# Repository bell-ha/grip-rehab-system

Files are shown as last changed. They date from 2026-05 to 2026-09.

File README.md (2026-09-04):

<div align="center">

# 악력 재활 시스템

**로드셀에서 읽은 힘을 실시간 신호처리로 다듬어, 게임과 소리로 되돌려주는 재활 시스템**







단국대학교 임베디드 시스템 과제 · 2인 팀 · 2026.04 ~ 2026.07

</div>

<div align="center">

<a href="https://www.youtube.com/watch?v=_I-ejlEAkNM">

</a>

<sub>데모 영상 — 로드셀을 쥐는 힘이 그대로 게임 입력이 된다 &nbsp;·&nbsp; 이미지를 누르면 영상이 열린다</sub>

<br><br>

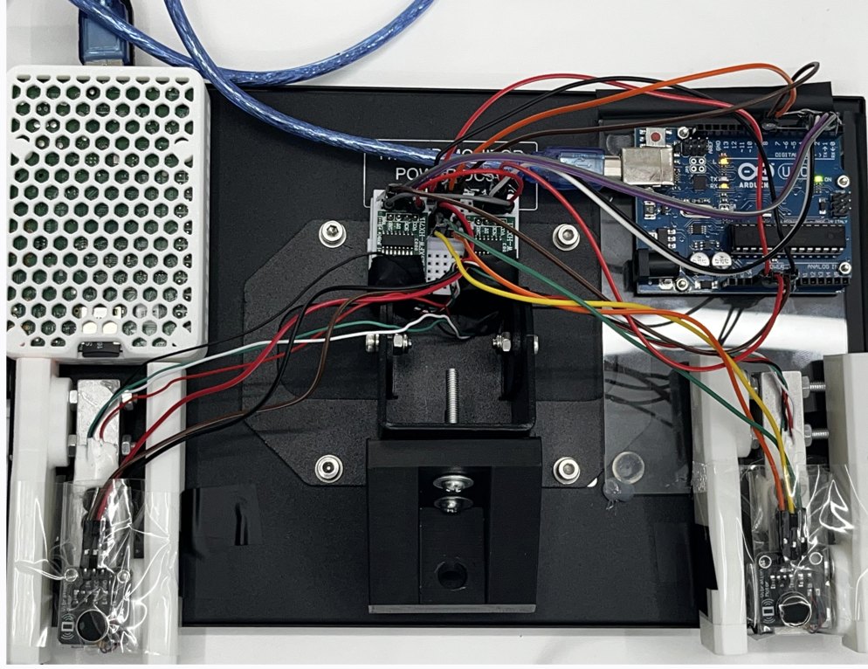
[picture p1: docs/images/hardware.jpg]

<br><sub>가운데 로드셀 마운트(3D 모델링·출력), 우측 상단 아두이노 우노, 그 아래 HX711 증폭 모듈.<br>좌우 진동 모터는 전류 부하 때문에 트랜지스터 구동으로 회로를 바꿨다</sub>

</div>

---

## 한눈에 보기

| | |
|---|---|
| **문제** | 악력 재활 훈련은 반복적이고 지루해서 지속률이 낮다 |
| **접근** | 양손 악력을 실시간으로 읽어 **게임 조작과 소리**로 되돌려준다 |
| **엔지니어링 초점** | 로드셀 원신호는 **노이즈와 스파이크로 그대로 쓸 수 없다.** 이걸 게임 입력으로 쓸 수 있는 신호로 만드는 것이 핵심 |
| **핵심 설계** | ① 4단 필터 파이프라인 ② 센서 3종 추상화 ③ Producer–Consumer 60 Hz 루프 |
| **결과** | 재활 게임 3종 + 악력 신디사이저 1종, 런처까지 손만으로 조작 |

> 이 저장소는 "게임 4개"가 아니라 **"센서 신호를 실시간 제어 입력으로 만드는 파이프라인"**에 관한 것이다.
> 게임은 그 파이프라인을 검증하는 응용이다.

---

## 목차

1. [왜 신호처리가 핵심인가](#1-왜-신호처리가-핵심인가)
2. [시스템 구성](#2-시스템-구성)
3. [신호처리 파이프라인](#3-신호처리-파이프라인)
4. [센서 3종 추상화](#4-센서-3종-추상화)
5. [실행 구조 (Producer–Consumer)](#5-실행-구조-producerconsumer)
6. [하드웨어](#6-하드웨어)
7. [응용 — 게임 3종 + 신디사이저](#7-응용--게임-3종--신디사이저)
8. [캘리브레이션](#8-캘리브레이션)
9. [실행 방법](#9-실행-방법)
10. [겪은 문제와 해결](#10-겪은-문제와-해결)

---

## 1. 왜 신호처리가 핵심인가

HX711 로드셀은 80 Hz로 값을 뱉지만, 그 원신호는 **게임 입력으로 바로 쓸 수 없다.**

- 손이 닿는 순간 **수십 kg짜리 스파이크**가 튄다
- 힘을 유지해도 값이 **미세하게 계속 진동**한다
- 손을 뗀 상태에서도 **0이 아니라 1 kg 근처를 떠돈다**

이 상태로 게임에 연결하면 캐릭터가 떨리고, 의도하지 않은 입력이 들어가고, 손을 뗐는데도 조작이 계속된다. **재활 대상자가 쓰는 시스템에서 이건 곧 사용 불가를 의미한다.**

그래서 이 프로젝트의 실제 과제는 게임을 만드는 것이 아니라, **원신호를 신뢰할 수 있는 제어 입력으로 바꾸는 것**이었다.

---

## 2. 시스템 구성

```mermaid
flowchart LR
    LC["로드셀 ×2<br/>좌 / 우"] --> ADC["HX711 ADC ×2<br/>80 Hz"]
    ADC --> ARD["Arduino Uno"]
    ARD -->|"UART 115200<br/>raw,raw"| PY["Python 런타임"]
    PY -->|"L1/L0/R1/R0"| ARD
    ARD --> VIB["진동 액츄에이터 ×2<br/>PWM"]

    PY --> FILT["4단 필터<br/>파이프라인"]
    FILT --> GAME["게임 루프<br/>60 Hz 고정 dt"]
    GAME --> SFX["오디오 피드백"]

    style FILT fill:#1f6feb,color:#fff
    style GAME fill:#1f6feb,color:#fff
```

**양방향 통신**이다. 센서 값을 받기만 하는 게 아니라, 게임 이벤트(두더지 명중, 벽 충돌)가 발생하면 진동 명령을 되돌려 보낸다.

---

## 3. 신호처리 파이프라인

원신호 → 제어 입력까지 4단계.

```mermaid
flowchart LR
    A["raw<br/>80 Hz"] --> B["① 스파이크 제거<br/>Δ &gt; 8 kg 폐기"]
    B --> C["② 중간값 필터<br/>N = 3"]
    C --> D["③ 이동평균<br/>N = 5"]
    D --> E["④ 데드존<br/>&lt; 1 kg → 0"]
    E --> F["kg"]

    style B fill:#1f6feb,color:#fff
    style C fill:#1f6feb,color:#fff
    style D fill:#1f6feb,color:#fff
    style E fill:#1f6feb,color:#fff
```

| 단계 | 파라미터 | 잡아내는 문제 |
|---|---|---|
| ① **스파이크 제거** | 이전 값 대비 **8 kg** 이상 급변 시 폐기 | 손이 닿는 순간의 순간 피크, 케이블 흔들림 |
| ② **중간값 필터** | 윈도우 **3** | 산발적 이상치. 평균과 달리 이상치에 끌려가지 않음 |
| ③ **이동평균** | 윈도우 **5** | 유지 구간의 미세 진동 |
| ④ **데드존** | **1 kg** 미만 → 0 | 손을 뗀 상태의 잔류값. "안 쥐고 있음"을 확실히 0으로 |

**순서가 설계 지점이다.** 스파이크를 먼저 버리지 않으면 중간값·이동평균 윈도우가 오염되고, 데드존을 먼저 적용하면 스파이크가 그대로 통과한다.

구현: [`common/sensor.py`](common/sensor.py)

---

## 4. 센서 3종 추상화

`GripSensor` 추상 인터페이스 하나에 구현 3개를 두었다.

| 구현 | 입력원 | 용도 |
|---|---|---|
| `MockGripSensor` | **키보드** (A/S 왼손, K/L 오른손) | **하드웨어 없이 게임 로직 개발·테스트** |
| `ArduinoGripSensor` | USB 시리얼 `raw,raw` | 일반 PC + Arduino |
| `RealGripSensor` | Raspberry Pi GPIO 직결 | 최종 배포 형태 |

**Mock 구현이 실용적으로 가장 중요했다.** 로드셀·Arduino가 없는 자리에서도 게임 로직과 렌더링을 그대로 개발할 수 있었고, 하드웨어 문제와 소프트웨어 문제를 분리해서 디버깅할 수 있었다.

Mock은 단순 키 입력이 아니라 실제 악력의 거동을 흉내 낸다 — 누르고 있으면 **9 kg/s로 차오르고**, 떼면 **8 kg/s로 감소**한다.

게임 코드는 어느 구현이 붙어 있는지 알지 못한다. 실행 플래그(`--arduino` / `--real` / 없음)만 바꾸면 된다.

---

## 5. 실행 구조 (Producer–Consumer)

센서는 **80 Hz**, 게임 루프는 **60 Hz**다. 주기가 다르고, 시리얼 읽기는 블로킹이다.

```
[센서 스레드]  시리얼 read → 필터 → Queue.put()      80 Hz
                                   │
[메인 스레드]  Queue.get_nowait() → 게임 로직 → 렌더  60 Hz 고정 dt
```

메인 루프에서 직접 시리얼을 읽으면 **읽기 지연이 그대로 프레임 드롭**이 된다. 센서 읽기를 별도 스레드로 분리하고 큐로 넘겨, 게임 루프가 센서 상태와 무관하게 일정한 dt를 유지하도록 했다.

고정 dt를 쓴 이유는, 물리 계산(풍선 팽창 속도, 우주선 관성)이 프레임 레이트에 따라 달라지면 **같은 힘을 줘도 기기마다 다르게 동작**하기 때문이다.

---

## 6. 하드웨어

### 배선

| 신호 | 왼손 | 오른손 |
|---|---|---|
| HX711 DOUT | D2 | D4 |
| HX711 SCK | D3 | D5 |
| 진동 액츄에이터 | D9 (PWM) | D10 (PWM) |

Raspberry Pi 직결 시 (BCM): DOUT `GPIO 5` / `GPIO 13`, SCK `GPIO 6` / `GPIO 19`

### 시리얼 프로토콜

직접 설계한 최소 프로토콜이다.

```
Arduino → PC   (10 ms 주기)      285400,291820\n     좌 raw, 우 raw
PC → Arduino   (이벤트 발생 시)   L1 / L0 / R1 / R0    좌우 진동 ON/OFF
```

파싱 비용을 줄이기 위해 고정 포맷 한 줄로 유지했고, 진동 명령은 상태 토글 방식이라 게임 쪽에서 타이머를 관리하지 않아도 된다.

### 3D 프린팅 마운트

로드셀을 손으로 쥘 수 있는 형태로 고정하기 위해 직접 모델링·출력했다.

| 파일 | 설명 |
|---|---|
| [`models/Base_1.stl`](models/Base_1.stl) | 센서 고정 베이스 |
| [`models/HX711_Load_Cell--Foot.stl`](models/HX711_Load_Cell--Foot.stl) | 로드셀 발판 |

---

## 7. 응용 — 게임 3종 + 신디사이저

파이프라인이 제대로 동작하는지는 **서로 다른 성격의 입력 요구**로 검증했다.

| 응용 | 요구하는 입력 특성 | 검증하는 것 |
|---|---|---|
| **풍선 키우기** | 목표값(≈15 kg)을 3초간 **유지** | 정상 상태의 안정성 — 진동이 남으면 유지 판정이 깨진다 |
| **두더지 잡기** | 짧고 강한 **순간 입력** | 응답 지연 — 필터가 과하면 반응이 늦어진다 |
| **우주 조종** | 양손 **차이값**으로 연속 조향 | 좌우 채널의 균형 — 한쪽만 편향되면 계속 휜다 |
| **악력 신디사이저** | 힘 → **연속적인 소리** | 미세 변화 해상도 — 떨림이 그대로 음정 흔들림이 된다 |

**신디사이저가 가장 가혹한 검증이었다.** 시각 피드백은 약간의 떨림을 눈치채기 어렵지만, 소리는 즉시 드러난다. 왼손이 볼륨(0.5~15 kg), 오른손이 주파수(2.3 kg → 220 Hz ~ 10 kg → 600 Hz, 로그 스케일)를 맡고, 기본파 + 2배음 + 3배음을 합성해 `aplay`로 끊김 없이 PCM 스트리밍한다.

**런처도 손으로 조작한다** — 왼손 0.3초 유지로 커서 왼쪽, 오른손으로 오른쪽, 양손 유지로 선택. 키보드 없이 시스템 전체를 쓸 수 있어야 재활 도구로 성립한다.

모든 게임 공통 종료 제스처: **양손 더블 펌프**(2초 내 2번 힘껏)

---

## 8. 캘리브레이션

로드셀은 개체마다 스케일이 다르고, 조립 상태에 따라 영점이 달라진다. 매번 손으로 맞출 수 없으므로 자동화했다.

**Arduino 모드 — 자동** (첫 실행 시)
```
1. 영점(Tare) 3초   손을 떼세요
2. 최대 악력 5초    최대한 세게 쥐세요
3. common/calibration.json 저장 → 이후 실행부터 재사용
```

**Raspberry Pi 직결 — 수동** ([`games/balloon_game/calibrate.py`](games/balloon_game/calibrate.py))
알고 있는 무게를 올려 스케일 팩터를 계산한다.

---

## 9. 실행 방법

```bash
python3 -m venv venv && source venv/bin/activate
pip install -r requirements.txt
```

Raspberry Pi에서 HX711 직결 시: `sudo apt-get install python3-dev alsa-utils && pip install hx711`

**런처** (전체 진입점)
```bash
cd games
DISPLAY=:0 python3 launcher.py --arduino   # Arduino USB
DISPLAY=:0 python3 launcher.py --real      # Pi HX711 직결
```

**개별 게임** — 3가지 모드 공통
```bash
python3 main.py            # Mock — 센서 없이 키보드로 (A/S 왼손, K/L 오른손)
python3 main.py --arduino  # Arduino USB 포트 자동 감지
python3 main.py --real     # Raspberry Pi GPIO 직결
```

**디버그 — 시리얼 모니터**
```bash
python3 measure/main.py    # 1/2 왼쪽 진동, 3/4 오른쪽 진동, q 종료
```

---

## 10. 겪은 문제와 해결

**진동 모터를 켜면 오른손 센서 값이 끊긴다**
진동 액츄에이터를 GPIO에 직결했더니 순간 전류가 몰려 HX711 읽기가 불안정해졌다. **NPN 트랜지스터(2N2222)를 통해 구동**하도록 회로를 바꿔 해결했다. 소프트웨어 문제로 보였지만 원인은 전원이었다.

**필터를 강하게 걸면 반응이 느려진다**
이동평균 윈도우를 키우면 신호는 매끄러워지지만 두더지 잡기의 반응속도가 떨어진다. **윈도우 3(중간값) + 5(이동평균)** 조합이 안정성과 지연 사이의 균형점이었다.

**포트 충돌**
Arduino IDE 시리얼 모니터가 열려 있으면 Python이 포트를 잡지 못한다. 포트 자동 감지를 넣되, 실패 시 원인을 명시하도록 했다.
포트 확인: macOS `ls /dev/cu.*` · Linux `ls /dev/ttyUSB*` `ls /dev/ttyACM*`

---

## 저장소 구조

```
├── sketch_jun11a.ino          # Arduino 펌웨어 (HX711 읽기 + 진동 제어)
├── common/                    # ★ 공용 계층
│   ├── sensor.py              #   GripSensor 추상화 + 필터 파이프라인
│   ├── sfx.py                 #   절차적 효과음 (numpy 합성)
│   └── fonts.py
├── games/
│   ├── launcher.py            #   메인 진입점 (악력으로 조작)
│   ├── balloon_game/          #   main / game_logic / renderer / calibrate
│   ├── Whack-A-Mole/          #   main / game_logic / renderer
│   ├── steering_game/         #   main / game_logic / renderer
│   └── synthesizer/           #   main / audio_engine / renderer
├── measure/main.py            # 시리얼 모니터 (디버그)
└── models/*.stl               # 3D 프린팅 마운트
```

`common/`에 하드웨어 접근과 신호처리를 한 벌만 두고, 그 위에 응용을 올리는 구조다. 센서 프로토콜이나 필터가 바뀌어도 `common/` 한 곳만 고치면 전체에 반영된다. 각 응용은 `main` / `game_logic` / `renderer`로 동일하게 분리했다.

---

<div align="center">

**이종하** · [GitHub](https://github.com/bell-ha) · [Portfolio](https://bell-ha.github.io)

</div>

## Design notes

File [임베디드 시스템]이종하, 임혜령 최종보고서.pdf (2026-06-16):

# 스마트 악력 측정 및 재활 게임 시스템

## 노인 재활을 위한 양손 악력 측정 기반

## 멀티 게임 시스템의 설계 및 구현

단국대학교 컴퓨터공학과

과목: 임베디드 시스템

학번 / 성명 : 32203482 이종하

학번 / 성명 : 32223872 임혜령

제출일 : 2026. 6. 16.

목차

1. 초록 | 1
2. 서론 | 2
3. 관련 연구 | 3
4. 시스템 설계 | 4
4.1 전체 아키텍처 | 4
4.2 하드웨어 설계 | 5
4.3 소프트웨어 설계 | 6
5. 구현 | 8
5.1 하드웨어 제작 | 8
5.2 핵심 코드 | 8
5.3 게임 구현 | 10
6. 결론 | 15
7. 참고문헌 | 16

## 1. 초록

본 연구는 손 악력이 저하된 노인 및 인지 기능 저하 환자를 대상으로, 재활 훈련을 게임의

형태로 제공하는 임베디드 악력 재활 게임기를 설계하고 구현한 결과를 기술한다.

제안하는 시스템은 두 개의 로드셀과 HX711 아날로그-디지털 변환(ADC) 모듈을 이용하여

양손의 악력을 동시에 측정하고, 아두이노가 이를 디지털 수치로 변환하여 USB UART

시리얼 통신으로 라즈베리 파이 4에 전송하며, 라즈베리 파이는 Pygame 기반의 게임

로직과 화면 출력을 담당한다. 아두이노는 악력 데이터 송신뿐 아니라 라즈베리

파이로부터 진동 명령을 수신하여 좌우 손잡이에 내장된 코인 진동 모터를 독립적으로

구동하는 양방향 시리얼 통신 구조를 채택하였다.

악력 신호의 미세한 떨림과 잡음을 제거하기 위하여 스파이크 필터, 중간값 필터, 이동

평균 필터, 데드존으로 구성된 다단계 신호 처리 파이프라인을 적용하였으며, 게임 진행

상태는 유한 상태 머신으로 모델링하였다. 사용자 상호작용은 마우스나 키보드 없이 오직

악력만으로 이루어지도록 설계하였다. 총 네 가지 게임, 즉 근력 조절 훈련의 '풍선 키우기',

반응 속도 및 좌우 인지 판단의 '두더지 잡기', 양손 힘의 차이를 이용하는 '우주선 조종',

그리고 악력을 음악적 표현으로 연결하는 '악력 신디사이저'를 구현하였다. 악력기 본체는

3D 프린팅으로 제작하였으며, 진동 모터를 손잡이 내부에 내장하여 시각·청각·촉각의 다중

감각 재활 UX를 실현하였다.

구현 결과 제안 시스템은 저비용 부품만으로 양손 악력을 안정적으로 측정하고 이를

다양한 게임 피드백에 실시간으로 반영함으로써, 노인 사용자가 흥미를 유지하며 재활에

참여할 수 있는 통합형 플랫폼으로서의 가능성을 확인하였다.

## 2. 서론

전 세계적으로 고령 인구의 비율이 급격히 증가하고 있으며, 우리나라 또한 초고령

사회로의 진입을 앞두고 있다. 고령화에 따라 뇌졸중, 파킨슨병, 근감소증 등으로 인한

상지(上肢) 기능 저하 환자가 늘어나고 있으며, 이들에게 있어 손의 악력은 일상생활 수행

능력 및 전반적 건강 상태를 가늠하는 중요한 지표로 알려져 있다. 특히 악력은 노인의

근력 수준뿐 아니라 사망률과 인지 기능 저하를 예측하는 임상적 지표로도 활용되고 있어,

지속적인 측정과 훈련의 필요성이 강조된다.

그러나 기존의 재활 방식은 여러 한계를 지닌다. 첫째, 단순 반복 동작 위주의 전통적 재활

운동은 환자에게 지루함을 유발하여 장기적인 참여 동기를 떨어뜨린다. 둘째, 측정과

훈련이 분리되어 있어 환자의 재활 경과를 정량적으로 누적·관리하기 어렵다. 셋째, 상용

재활 장비는 고가이며 대형 의료기관에 한정되어 있어 접근성이 낮다. 넷째, 인지 기능이

저하된 노인의 경우 복잡한 조작이나 규칙을 요구하는 장비는 사용 자체가 어렵다.

본 연구는 이러한 문제를 해결하기 위하여 측정·훈련·피드백을 하나로 통합한 저비용 악력

재활 게임 시스템을 제안한다. 제안 시스템은 (1) 로드셀과 HX711을 이용해 양손 악력을

정밀하게 측정하고, (2) 측정값을 네 가지 게임의 즉각적 시각·촉각 피드백으로 변환하여

재미와 동기를 부여하며, (3) 악력만으로 모든 상호작용이 가능하도록 설계하여 인지 저하

환자의 사용성을 확보하는 것을 목표로 한다. 또한 아두이노와 라즈베리 파이 간 시리얼

통신을 양방향으로 구성하여 진동 피드백을 실현함으로써, 시각·청각·촉각의 다중 감각

재활 UX를 하나의 플랫폼에 통합하였다.

## 3. 관련 연구

게임을 재활 치료에 접목하는 기능성 게임 연구는 환자의 참여 동기와 치료 순응도를

높이는 효과적인 수단으로 주목받아 왔다. 이정훈과 김민수[1]는 뇌졸중 환자의 상지

재활을 위한 기능성 게임 콘텐츠를 개발하고 그 효과를 분석하였으며, 단순 반복 운동에

비해 게임 기반 훈련이 환자의 자발적 참여 시간과 만족도를 유의하게 향상시킴을

보고하였다.

Lange 등[2]은 저가형 동작 인식 센서를 활용하여 균형 재활 도구를 개발하고

평가함으로써, 고가의 전용 장비 없이도 상용 센서를 통해 재활 시스템을 구축할 수 있음을

제시하였다. 이는 본 연구에서 로드셀과 HX711 같은 저가 부품으로 재활 게임기를 구성한

설계 철학과 맥을 같이한다. 또한 노인의 인지 기능 향상을 위한 기능성 게임을 설계하고

그 효과를 검증하여, 게임의 반응 속도 요소와 판단 과제가 노인의 인지 재활에 기여할 수

있음을 보였다. Bark 등[3]은 재활 훈련에서 햅틱 피드백의 효과를 연구하여, 촉각 자극이

운동 학습 및 신경 재활에 긍정적 영향을 미침을 확인하였다.

선행 연구들은 게임 기반 재활의 효과와 저비용 구현 가능성을 각각 입증하였으나, 대부분

동작 인식이나 화면 터치 기반 상호작용에 초점을 두었으며, 양손 악력을 직접적인 입력

수단으로 삼아 측정과 훈련을 동시에 수행하면서 햅틱 피드백까지 통합한 시스템은

상대적으로 부족하였다. 본 연구는 이러한 공백을 보완하고자 한다.

## 4. 시스템 설계

### 4.1 전체 아키텍처

제안 시스템은 데이터 수집 계층과 게임 처리 계층으로 명확히 분리된다. 물리적 악력은

로드셀에 의해 미세한 전압 신호로 변환되고, HX711 모듈이 이를 24비트 디지털 값으로

증폭·변환한다. 아두이노는 두 개의 HX711로부터 raw ADC 값을 읽어 USB UART 시리얼

통신(115200 baud)으로 라즈베리 파이에 전송한다.

기존 악력 데이터 전송 방향(아두이노 → 라즈베리 파이)에 더해, 본 시스템은 라즈베리

파이에서 아두이노로 진동 제어 명령을 역방향으로 전송하는 양방향 시리얼 통신을

구현하였다. 게임 이벤트 발생 시 라즈베리 파이가 "L1" / "L0" / "R1" / "R0" 형식의 명령을

전송하면, 아두이노가 이를 수신하여 왼손(GPIO 9번) 또는 오른손(GPIO 10번)의 코인 진동

모터를 독립적으로 ON/OFF 제어한다. 전체 데이터 흐름은 [그림 1]과 같다.

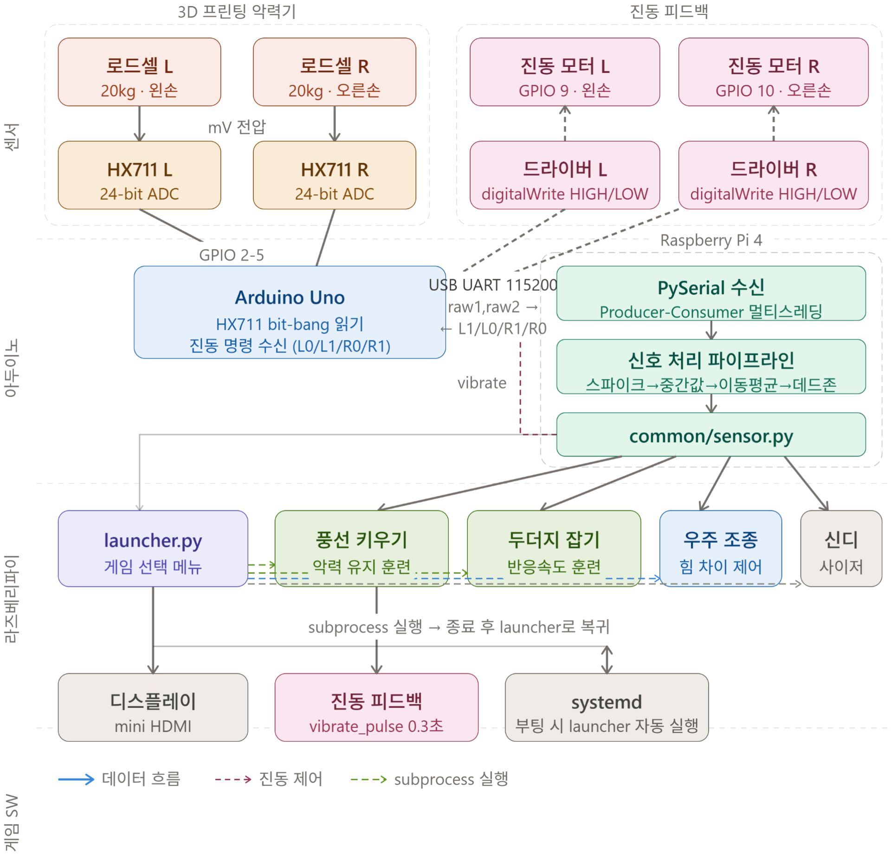
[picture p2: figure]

[그림 1] 시스템 전체 구성도 (양방향 시리얼 통신 포함)

이와 같은 계층 분리는 하드웨어 의존부와 응용부(게임 로직)를 독립적으로 개발·검증할 수

있게 한다. 본 프로젝트에서는 추상 인터페이스인 GripSensor를 정의하고, 실제

하드웨어용 구현체와 키보드 시뮬레이션용 MockGripSensor를 동일 인터페이스로

제공함으로써, 하드웨어 없이도 PC에서 게임 로직을 개발할 수 있도록 하였다. 각

GripSensor 구현체는 백그라운드 스레드에서 센서 값을 지속적으로 읽어들이는 Producer

역할을 수행하고, 게임 루프는 get() 메서드를 통해 최신 값을 읽는 Consumer로 동작하는

Producer-Consumer 구조를 채택하여, 센서 통신 지연이 게임 루프의 프레임 속도에

영향을 주지 않도록 하였다.

### 4.2 하드웨어 설계

로드셀은 외력에 의한 미소 변형을 스트레인 게이지의 저항 변화로 검출하는 센서로,

휘트스톤 브리지 회로를 통해 변형량에 비례하는 미세 전압을 출력한다. 본 시스템은 최대

측정 범위 20 kg의 로드셀 두 개를 사용하여 왼손과 오른손의 악력을 각각 독립적으로

측정한다. HX711은 로드셀 계측에 특화된 24비트 정밀 ADC로, 내부 저잡음

PGA(Programmable Gain Amplifier)를 통해 채널 A 기준 최대 128배의 게인으로 신호를

증폭한다.

진동 피드백 모듈은 코인형 진동 모터 두 개로 구성된다. 각 모터는 별도의 구동 회로 없이

아두이노의 GPIO 9번(왼손)과 10번(오른손)에 직접 연결되며, 라즈베리 파이로부터 수신한

명령에 따라 digitalWrite를 통해 HIGH/LOW로 독립적으로 ON/OFF 제어된다. 진동 모터는

3D 프린팅된 손잡이 내부에 내장되어, 게임 이벤트 발생 시 손을 통해 촉각 피드백을 직접

전달한다. [그림 2]는 로드셀–HX711–아두이노–진동 모터 구조를 나타낸다.

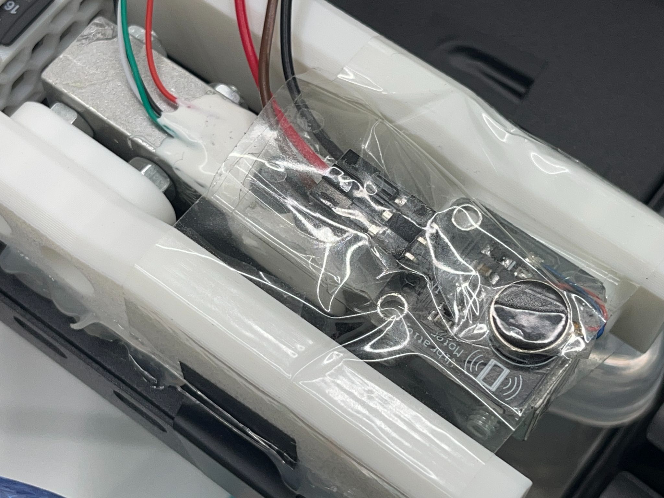
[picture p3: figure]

[그림 2] 로드셀–HX711–아두이노–진동 모터

악력기 본체는 손으로 쥐는 힘이 로드셀의 수직 방향으로 온전히 전달되도록 지지대

구조를 설계하였다. 로드셀은 외팔보(cantilever) 형태로 장착되며, 진동 모터는 손잡이

내부 공동(cavity)에 매립되어 케이블과 함께 본체에 고정된다. 본체와 고정 베이스는 3D

프린팅으로 출력하였다.

### 4.3 소프트웨어 설계

소프트웨어는 (1) 아두이노 펌웨어, (2) 신호 처리 파이프라인의 두 부분으로 구성된다.

(1) 아두이노 펌웨어

아두이노 펌웨어는 외부 라이브러리에 의존하지 않고 HX711의 통신 프로토콜을 직접

구현(bit-banging)하였다. DOUT 핀이 LOW가 되면 변환 완료로 판단하고, SCK 핀에 클럭

펄스를 인가하며 24비트를 MSB부터 순차적으로 읽어들인 뒤, 25번째 펄스로 다음 변환의

채널과 게인(채널 A, 게인 128)을 설정한다.

진동 제어 기능은 비블로킹 시리얼 수신으로 구현하였다. 메인 루프에서 악력 읽기 및

전송과 병행하여 시리얼 버퍼를 폴링하며, 2바이트 명령이 완성되면 해당 핀을 즉시

HIGH/LOW로 제어한다. 이를 통해 악력 전송 주기(10 ms)에 영향을 주지 않으면서 진동

명령에 즉각 반응할 수 있다.

(2) 신호 처리 파이프라인

로드셀 신호는 온도 변화와 진동에 민감하여 미세한 떨림과 순간적 스파이크가 발생한다.

이를 보정하기 위해 라즈베리 파이 측에서 80 Hz로 구동되는 4단계 신호 처리

파이프라인을 적용한다.

- 스파이크 필터: 직전 값 대비 8 kg 이상 급격히 상승한 값을 직전 값으로 대체하여

순간 잡음 제거.

- 중간값 필터: 3개 표본의 중간값을 취하여 돌발 잡음에 강인성 부여 (윈도우 크기

N=3)

- 이동 평균 필터: 5개 표본의 평균으로 신호를 평활화하여 화면 진동 방지 (윈도우

크기 N=5)

- 데드존: 1 kg 이하의 미세 신호를 0으로 처리하여 손을 떼었을 때의 표류 억제

## 5. 구현

### 5.1 하드웨어 제작

악력기 본체와 센서 고정 베이스는 3D 모델링 후 3D 프린터로 출력하였다. 출력된 부품에

로드셀을 외팔보 형태로 장착하고, 로드셀의 단자를 HX711 모듈에 납땜하여 연결하였다.

코인 진동 모터는 손잡이 공동 내부에 매립하고 아두이노 GPIO 9번(왼손)/10번(오른손)

핀에 연결하였다. 양손 측정을 위해 동일한 구조의 악력기 두 개를 제작하였다. [그림 3]는

3D 모델을, [그림 4]는 완성된 하드웨어 형상을 보여준다.

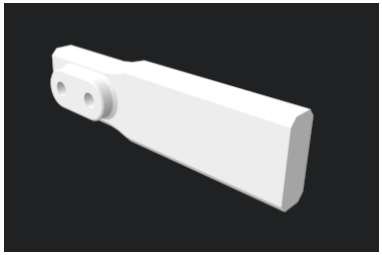
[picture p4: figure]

[그림 3] 3D 모델

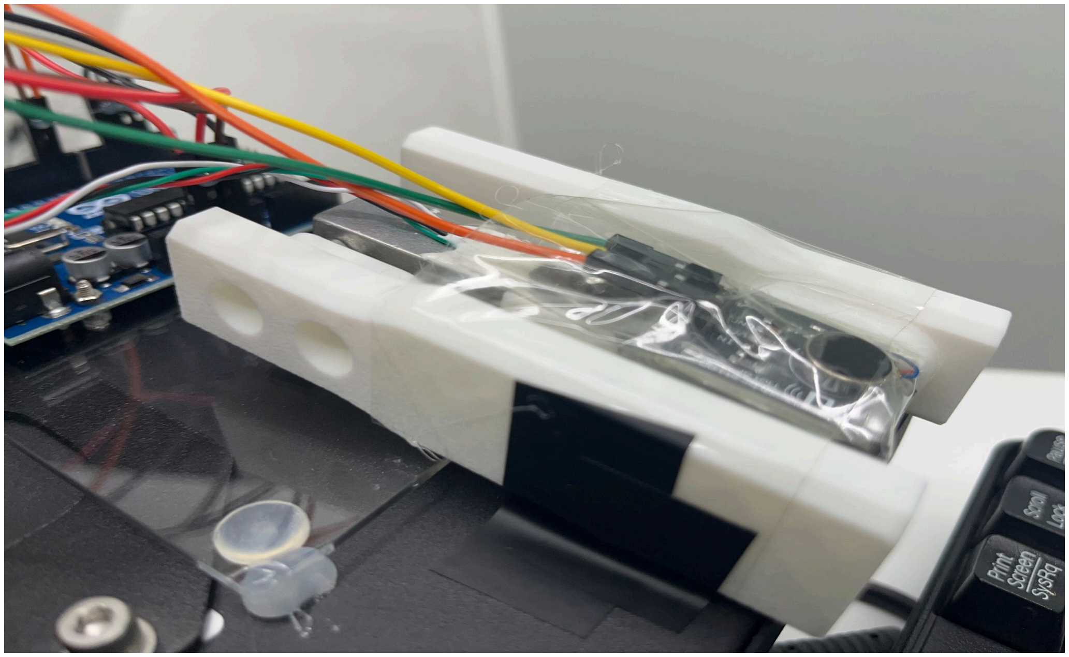
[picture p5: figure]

[그림 4] 로드셀·진동 모터 장착

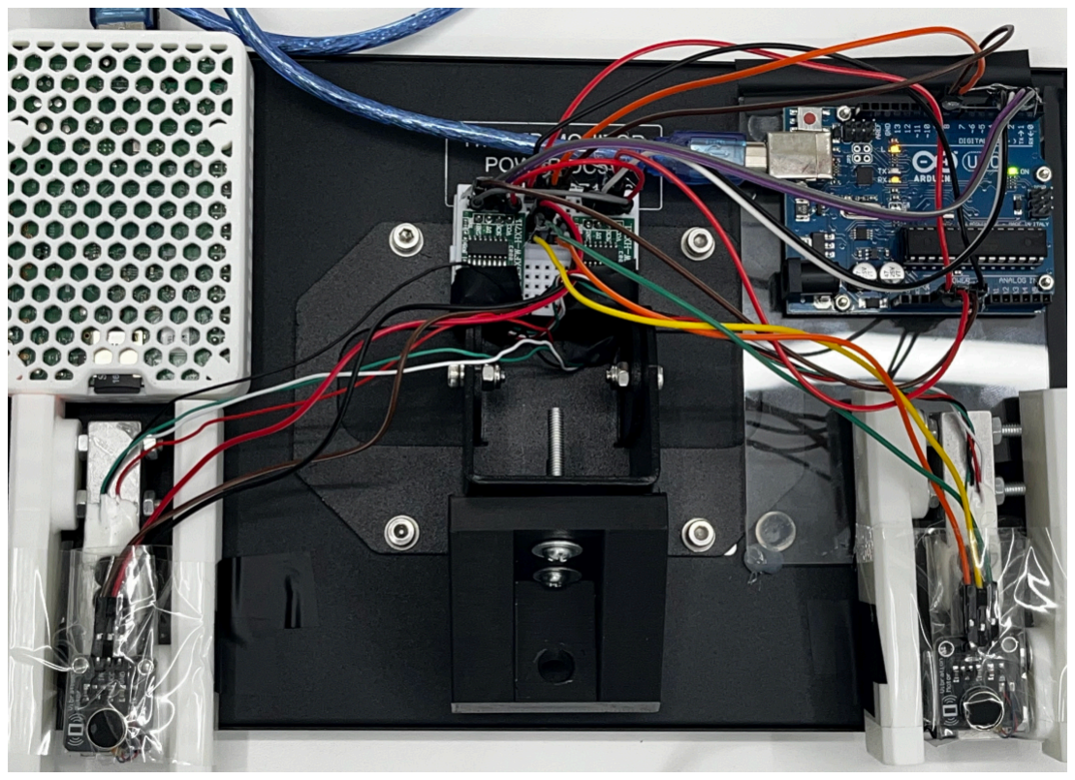
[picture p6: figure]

[그림 5] 조립이 완료된 하드웨어 본체

### 5.2 핵심 코드

본 절에서는 시스템의 핵심이 되는 세 가지 코드, 즉 (a) 아두이노의 HX711 직접 읽기 루틴,

(b) 아두이노의 진동 제어 시리얼 수신 루틴, (c) 라즈베리 파이의 신호 처리 파이프라인을

발췌하여 제시한다.

(a) 아두이노 — HX711 비트뱅잉(bit-banging) 읽기 (C)

// HX711에서 24비트 raw 값 1개 읽기 (외부 라이브러리 미사용) long hx711_read(int dout, int sck) {
while (digitalRead(dout) == HIGH); // 변환 완료 대기 long value = 0;
for (int i = 0; i < 24; i++) { | // MSB부터 24비트 수신
digitalWrite(sck, HIGH);
delayMicroseconds(1);
value = (value << 1) | digitalRead(dout);
digitalWrite(sck, LOW);
delayMicroseconds(1);
}
digitalWrite(sck, HIGH); | // 25번째 펄스: 채널 A, 게인
128
delayMicroseconds(1);
digitalWrite(sck, LOW);
if (value & 0x800000) | // 24비트 2의 보수
value |= 0xFF000000;
return value;

}

[코드 1] 라이브러리 없이 구현한 HX711 24비트 읽기 루틴

(b) 아두이노 — 진동 제어 비블로킹 시리얼 수신 (C)

// 포맷: "L1\n"→왼쪽ON "L0\n"→왼쪽OFF "R1\n"→오른쪽ON "R0\n"→오른쪽OFF void handle_serial() {
while (Serial.available() > 0) {
char c = (char)Serial.read(); if (c == '\n' || c == '\r') { if (serial_pos == 2) {
char side = serial_buf[0]; char val = serial_buf[1];
if | (side=='L' && val=='1')
digitalWrite(LEFT_VIB, HIGH); else if (side=='L' && val=='0') digitalWrite(LEFT_VIB, LOW); else if (side=='R' && val=='1') digitalWrite(RIGHT_VIB, HIGH); else if (side=='R' && val=='0') digitalWrite(RIGHT_VIB, LOW); }
serial_pos = 0;
} else if (serial_pos < 7) { serial_buf[serial_pos++] = c; } }
}

[코드 2] 진동 모터 제어를 위한 비블로킹 시리얼 수신 루틴

(c) 라즈베리 파이 — GripFilter 신호 처리 파이프라인 (Python)

def process(self, raw: float) -> float:
# 1. 스파이크 필터: 직전 값 대비 급변 시 직전 값으로 대체

if abs(raw - self._prev) > SPIKE_THRESHOLD: # SPIKE_THRESHOLD = 8.0 kg
raw = self._prev
self._prev = raw
# 2. 중간값 필터: 윈도우 내 표본의 중간값 (N=3) self._raw_buf.append(raw)

median = sorted(self._raw_buf)[len(self._raw_buf) // 2] # 3. 이동 평균 필터: 연속 표본 평균으로 평활화 (N=5) self._avg_buf.append(median)
avg = sum(self._avg_buf) / len(self._avg_buf)
# 4. 데드존: 1 kg 이하의 미세 신호는 0 처리

return 0.0 if avg < DEADZONE_KG else round(avg, 2)

[코드 3] 스파이크 → 중간값 → 이동 평균 → 데드존 4단계 필터 파이프라인

### 5.3 게임 구현

사용자의 흥미 수준과 재활 목적을 고려하여 네 가지 게임을 구현하였다. 모든 게임은 공통

센서 추상화 계층(common/sensor.py)을 통해 동일한 인터페이스로 악력 데이터를

수신하며, 런처(launcher.py)에서 악력 제스처만으로 게임을 선택하고 시작할 수 있다.

(1) 풍선 키우기 — 근력 조절 훈련

입문용 튜토리얼 성격의 게임이다. 왼손은 왼쪽 풍선, 오른손은 오른쪽 풍선과 1:1로

대응되며, 쥐는 힘의 세기에 비례하여 풍선이 커진다. 목표 크기(15 kg 기준)에 맞추어 3초

동안 악력을 유지하면 성공으로 처리되고, 22 kg 이상을 가하면 풍선이 터진다. '세게 쥐면

풍선이 커진다'는 직관적 피드백만으로 이해할 수 있어 인지 저하 노인에게 적합하며, 목표

악력의 정밀한 유지를 통해 근력 조절 훈련 효과를 제공한다.

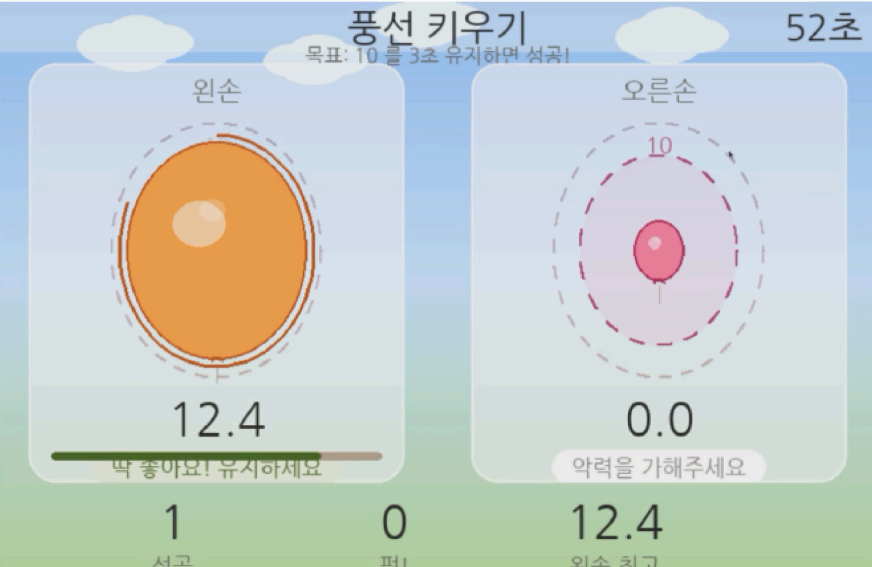
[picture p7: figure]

[그림 6] '풍선 키우기' 게임 실행 화면

(2) 두더지 잡기 — 반응 속도 및 좌우 인지 훈련

반응 속도와 좌우 인지 판단을 함께 훈련하는 게임이다. 두더지가 왼쪽·가운데·오른쪽

구멍에 무작위로 출현하며, 해당 위치의 손으로 일정 악력 이상을 가하면 두더지를 잡을 수

있다. 가운데 구멍에는 양손을 동시에 사용해야 한다. 연속 성공 시 콤보 점수가 부여되고,

게임 진행에 따라 출현 속도가 빨라져 난이도가 상승한다.

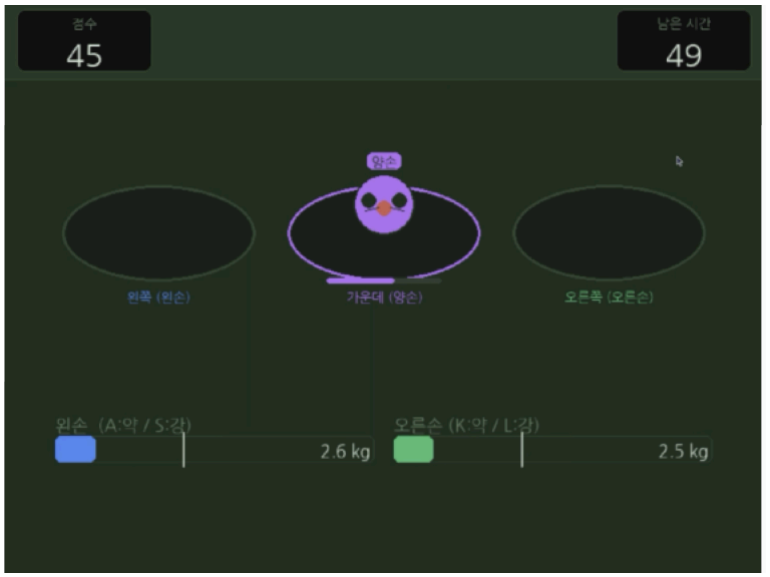
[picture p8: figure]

[그림 7] '두더지 잡기' 게임 실행 화면

(3) 우주선 조종 — 양손 협응 및 균형 훈련

양손의 힘 차이를 이용하여 우주선을 조종하는 게임이다. 오른손 악력에서 왼손 악력을 뺀

순 힘이 우주선의 수평 이동 방향과 속도를 결정하며, 두 손이 동일한 힘이면 우주선은

중앙으로 복귀한다. 터널은 시간이 지날수록 좁아지며(초기 폭 350 px → 최소 130 px),

벽에 충돌하면 목숨이 감소한다(3개). 60초 생존이 목표이다. 벽 충돌 시 양손 진동 모터가

즉시 활성화되어 촉각 피드백을 제공한다.

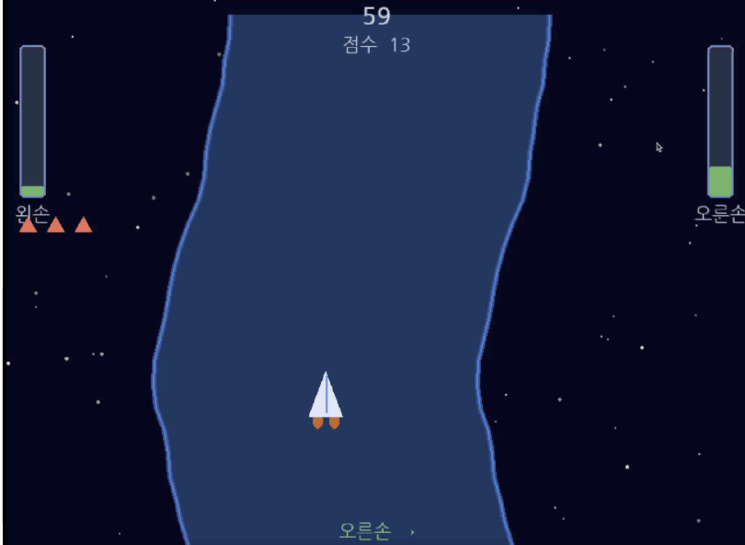
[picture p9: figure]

[그림 8] '우주선 조종' 게임 실행 화면

(4) 악력 신디사이저 — 창의적 감각 훈련

악력을 음악적 표현으로 연결하는 비게임형 훈련 콘텐츠이다. 왼손 악력은

음량(0~100%)을 제어하고, 오른손 악력은 2옥타브 범위의 음 높이를 제어한다.

sounddevice 라이브러리를 통해 실시간으로 사인파를 생성·재생하며, 현재 활성화된

주파수의 시각화 화면에서 실시간으로 표시된다. 규칙 없이 자유롭게 악력으로 음악을

만드는 경험을 통해 훈련 부담감을 낮추고 음악적 피드백을 통한 인지 자극 효과를

기대한다.

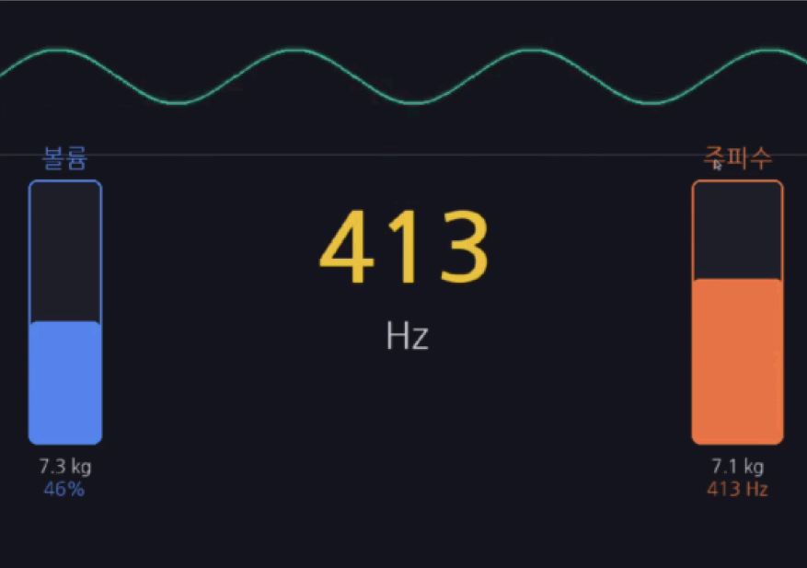
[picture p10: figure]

[그림 9] '악력 신디사이저' 실행 화면

## 6. 결론

본 연구에서는 노인 및 인지 저하 환자를 위한 양손 악력 기반 재활 게임 시스템을

설계하고 구현하였다. 로드셀과 HX711, 아두이노, 라즈베리 파이를 계층적으로 결합하여

측정·처리·표현의 역할을 명확히 분리하였고, 4단계 신호 처리 파이프라인과 규칙 기반

게임 로직을 통해 안정적이고 직관적인 재활 게임을 구현하였다. 특히 양방향 시리얼

통신을 통해 코인 진동 모터를 게임 이벤트에 연동함으로써, 시각·청각·촉각의 다중 감각

재활 UX를 하나의 저비용 플랫폼에 통합하였다. 풍선 키우기, 두더지 잡기, 우주선 조종,

악력 신디사이저의 네 가지 게임을 통해 근력 조절, 반응 속도, 양손 협응, 창의적

표현이라는 다양한 재활 목적을 하나의 시스템에서 제공할 수 있음을 보였다.

다만 본 시스템은 다음과 같은 한계를 가진다. 첫째, 로드셀의 특성상 온도 변화와 장시간

사용에 따른 영점 표류가 발생할 수 있어 주기적인 재캘리브레이션이 필요하다. 둘째, 재활

경과를 누적·저장하는 영속적 데이터 로깅 기능의 완전한 구현이 향후 과제로 남아 있다.

셋째, 임상적 효과에 대한 정량적 검증은 충분한 표본을 대상으로 한 실험을 통해 보완될

필요가 있다. 넷째, 촉각 피드백을 위해 손잡이 내부에 소형 진동 모터를 탑재하였으나,

GPIO 출력 전류의 불안정성으로 인해 간헐적 오작동이 발생하였다. 향후 트랜지스터 기반

구동 회로를 적용하여 안정적인 햅틱 피드백을 구현할 필요가 있다.

향후 연구로는 다음을 제안한다. 첫째, 재활 이력 데이터를 클라우드에 연동하여 보호자가

웹 대시보드로 재활 현황을 확인할 수 있는 헬스케어 융합 기능을 추가할 수 있다. 둘째,

힘을 주는 속도와 유지 시간 등의 데이터를 수집하여 근력 저하 속도나 인지 상태를

예측하는 머신러닝 기반 악력 패턴 분석을 시도할 수 있다. 셋째, TTS(Text-to-Speech)를

도입하여 시각적 안내를 음성으로도 제공함으로써 시각 장애 또는 저시력 노인의

접근성을 높일 수 있다.

## 7. 참고문헌

[1] 이정훈, 김민수, "뇌졸중 환자의 상지 재활을 위한 기능성 게임 콘텐츠의 효과 분석,"

한국게임학회 논문지, vol. 18, no. 4, pp. 33–42, 2018.

[2] B. Lange, C.-Y. Chang, E. Suma, B. Newman, A. S. Rizzo, and M. Bolas, "Development

and evaluation of low cost game-based balance rehabilitation tool using the

Microsoft Kinect sensor," in Proc. Annu. Int. Conf. IEEE Eng. Med. Biol. Soc. (EMBC),

Boston, MA, USA, 2011, pp. 1831–1834.

[3] K. Bark, J. Khanna, R. Irwin, J. Kapur, and K. Mukherjee, "Lessons in using vibrotactile

feedback to guide slow-movements," in Proc. IEEE World Haptics Conf., Istanbul,

Turkey, 2011, pp. 579–584.

[4] S. McCallum, "Gamification and serious games for personalized health," Studies in

Health Technology and Informatics, vol. 177, pp. 85–96, 2012.

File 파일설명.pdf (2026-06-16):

### 파일 설명

sketch_jun11a.ino – 아두이노에 업로드한 코드

requirments.txt – 전체적인 시스템을 위해 필요한 모듈

models/Base_1.stl – 하드웨어 제작에 사용한 모델

common 폴더 – 하드웨어 조작에 필요한 파일들

games 폴더 –게임 소스코드

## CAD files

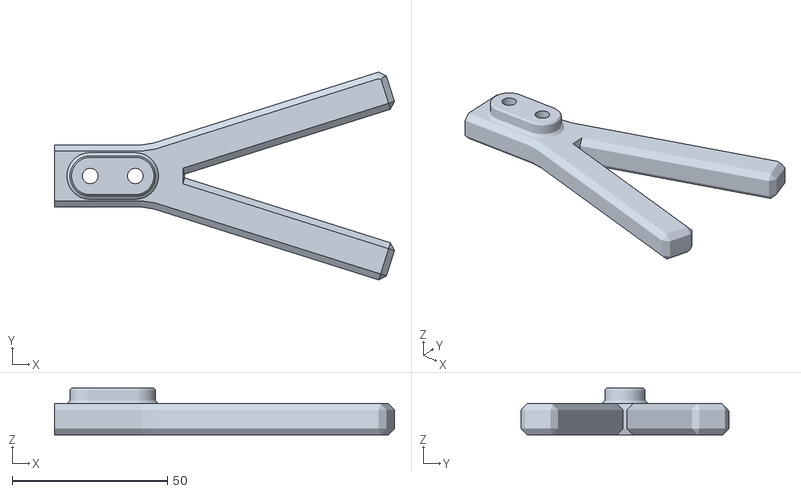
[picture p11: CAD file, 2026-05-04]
models/HX711_Load_Cell--Foot.stl
109.5 x 66.9 x 15.0

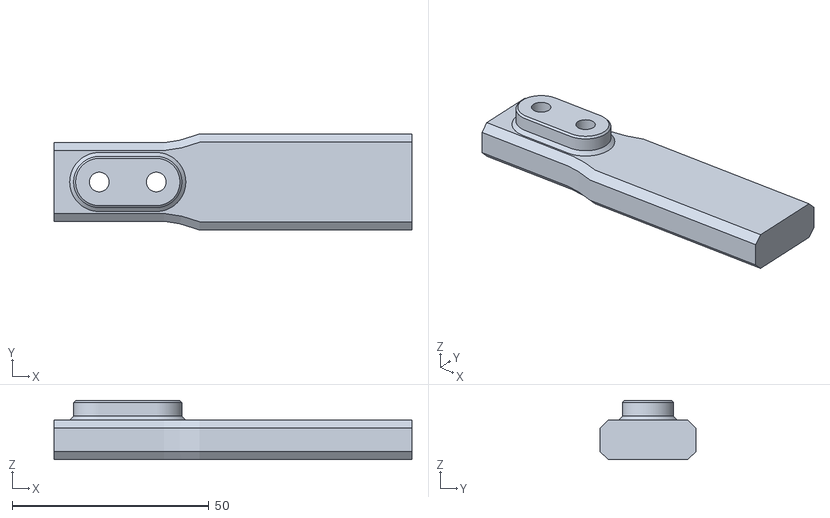
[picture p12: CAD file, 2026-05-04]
models/Base_1.stl
91.0 x 24.4 x 15.0

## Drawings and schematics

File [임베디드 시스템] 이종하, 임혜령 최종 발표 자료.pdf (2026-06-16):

# 악력 재활 게임기

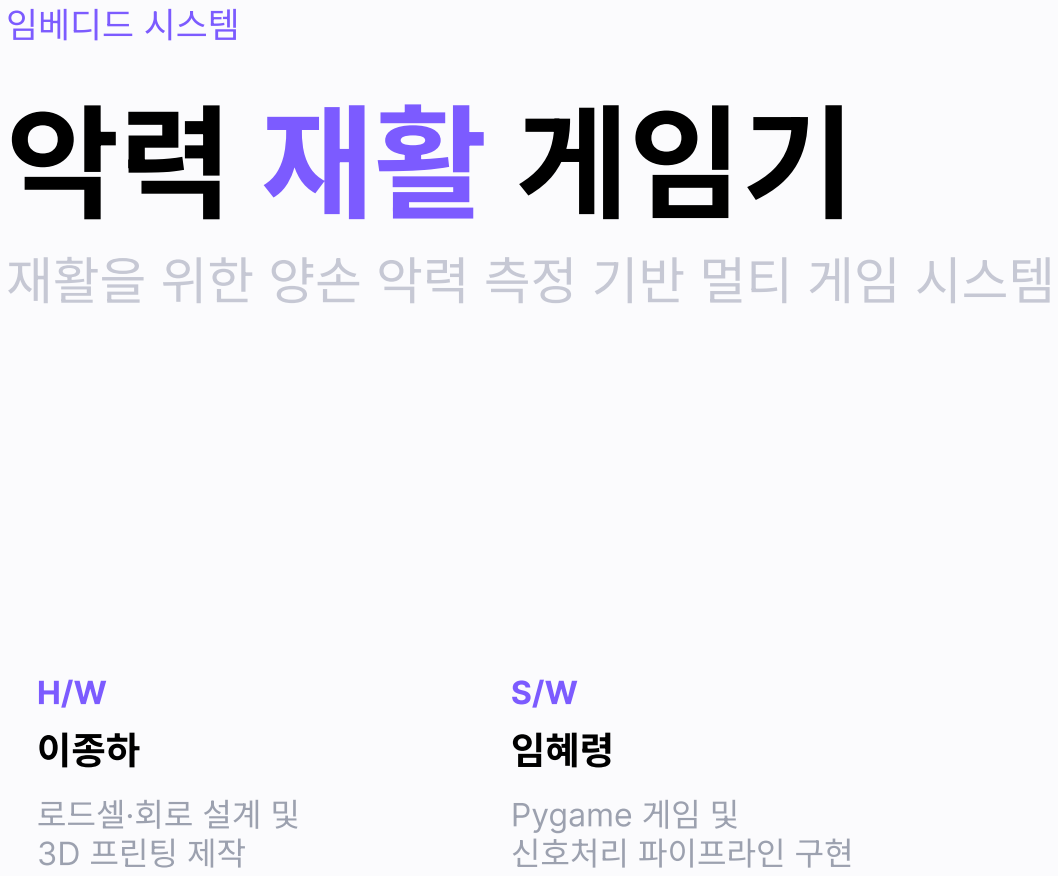
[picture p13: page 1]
임베디드 시스템

재활을 위한 양손 악력 측정 기반 멀티 게임 시스템

이종하
로드셀·회로 설계 및
3D 프린팅 제작

임혜령
Pygame 게임 및
신호처리 파이프라인 구현

# 개발 동기 및 필요성

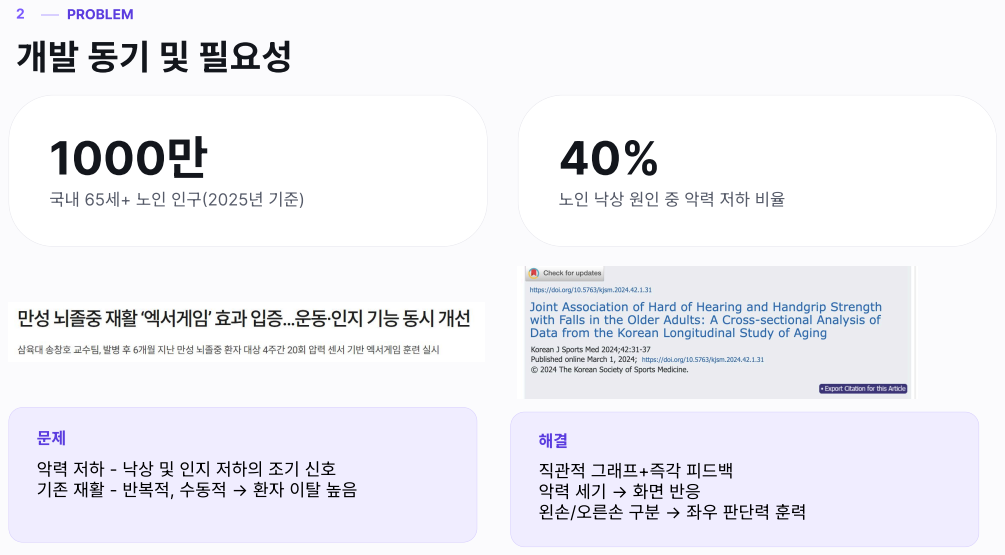
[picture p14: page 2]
PROBLEM

악력 저하 - 낙상 및 인지 저하의 조기 신호
기존 재활 - 반복적, 수동적 → 환자 이탈 높음

직관적 그래프+즉각 피드백
왼손/오른손 구분 → 좌우 판단력 훈력

# 시스템 아키텍처

## 로드셀 → HX711 → Arduino → Raspberry Pi 4 → Display

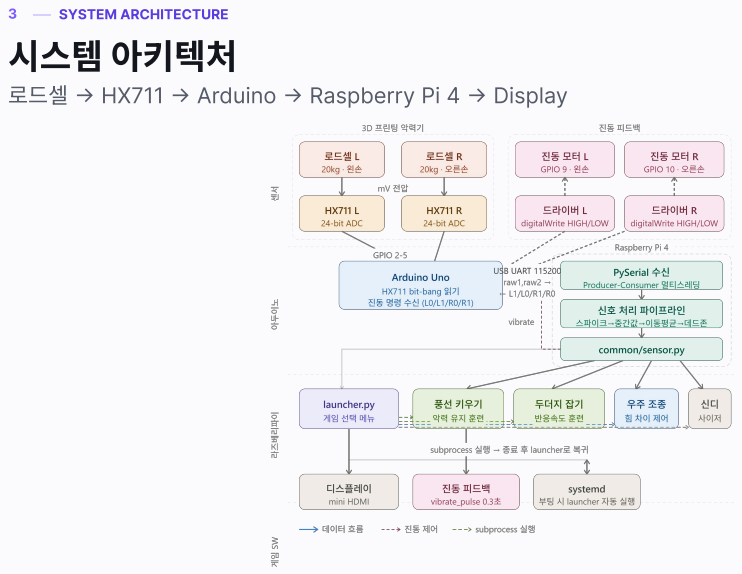
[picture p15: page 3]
SYSTEM ARCHITECTURE

# 하드웨어 구성

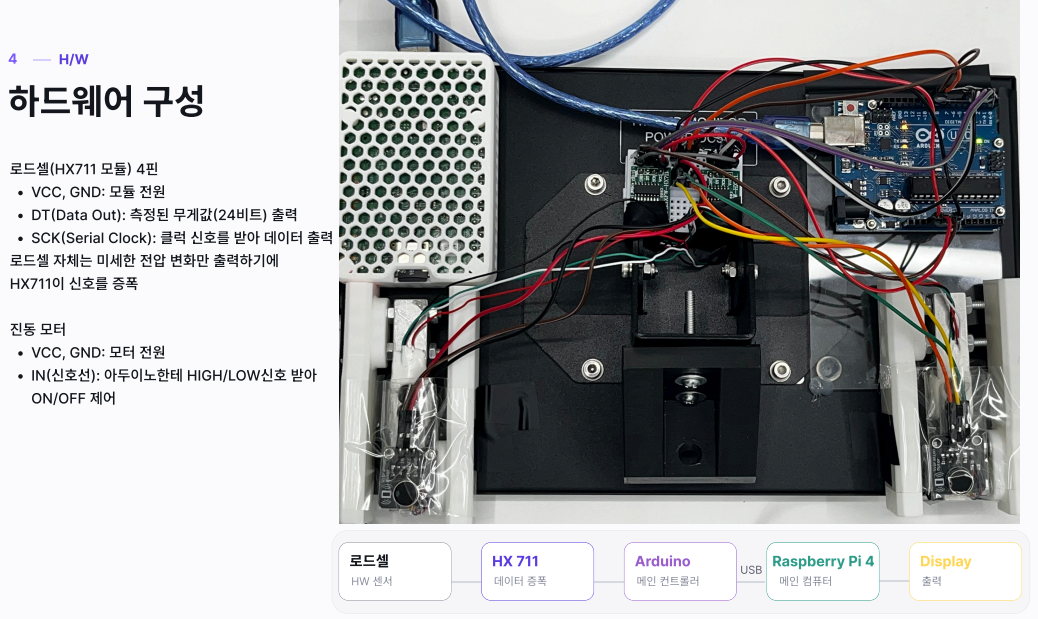
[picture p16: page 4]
로드셀; 데이터 증폭; Arduino; 메인 컨트롤러; 메인 컴퓨터; Display

로드셀(HX711 모듈) 4핀
VCC, GND: 모듈 전원
DT(Data Out): 측정된 무게값(24비트) 출력
SCK(Serial Clock): 클럭 신호를 받아 데이터 출력
로드셀 자체는 미세한 전압 변화만 출력하기에
HX711이 신호를 증폭

VCC, GND: 모터 전원
IN(신호선): 아두이노한테 HIGH/LOW신호 받아
ON/OFF 제어

USB Raspberry Pi 4

# 주요 게임 컨텐츠

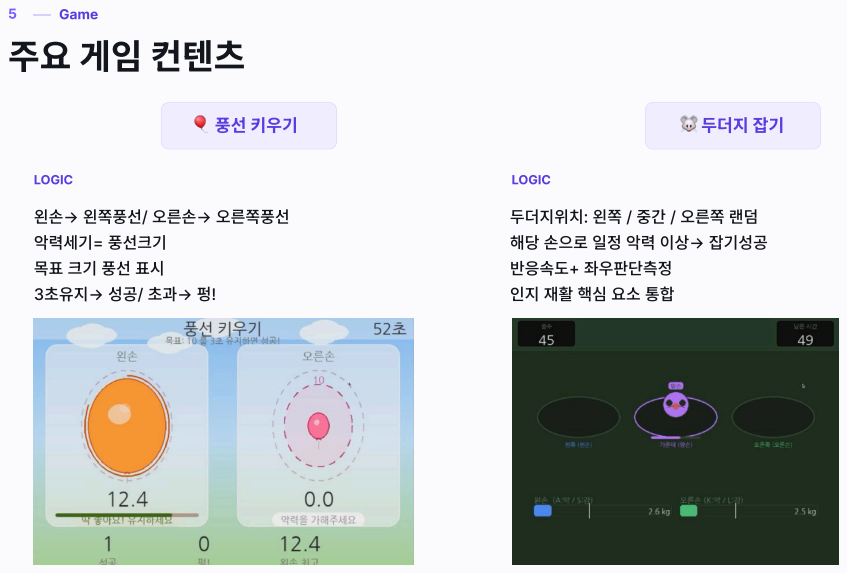
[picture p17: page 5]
Game; 🎈 풍선 키우기; 🐭 두더지 잡기; LOGIC

왼손→ 왼쪽풍선/ 오른손→ 오른쪽풍선
악력세기= 풍선크기
3초유지→ 성공/ 초과→ 펑!

두더지위치: 왼쪽 / 중간 / 오른쪽 랜덤
해당 손으로 일정 악력 이상→ 잡기성공
반응속도+ 좌우판단측정

# 주요 게임 컨텐츠

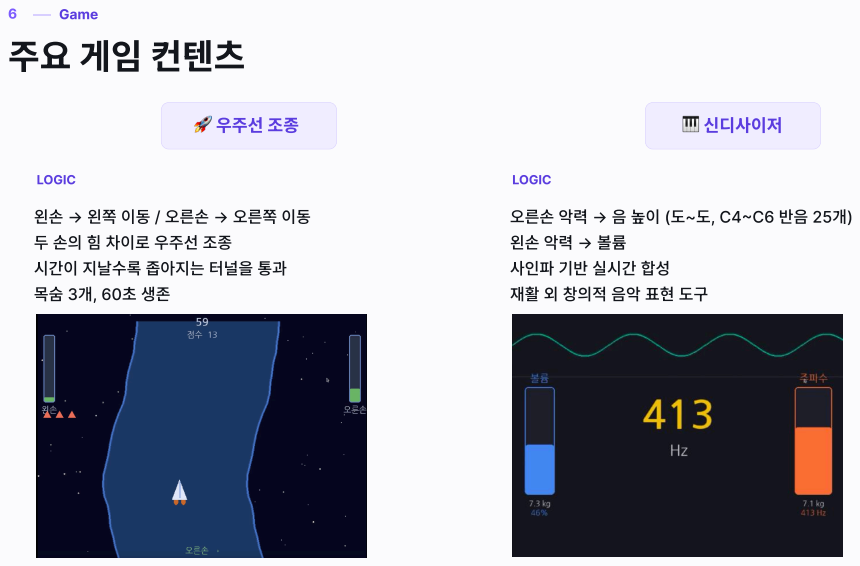
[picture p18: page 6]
Game; 🚀 우주선 조종; 🎹 신디사이저; LOGIC

왼손 → 왼쪽 이동 / 오른손 → 오른쪽 이동
두 손의 힘 차이로 우주선 조종
시간이 지날수록 좁아지는 터널을 통과

오른손 악력 → 음 높이 (도~도, C4~C6 반음 25개)
사인파 기반 실시간 합성
재활 외 창의적 음악 표현 도구

# 데모 영상

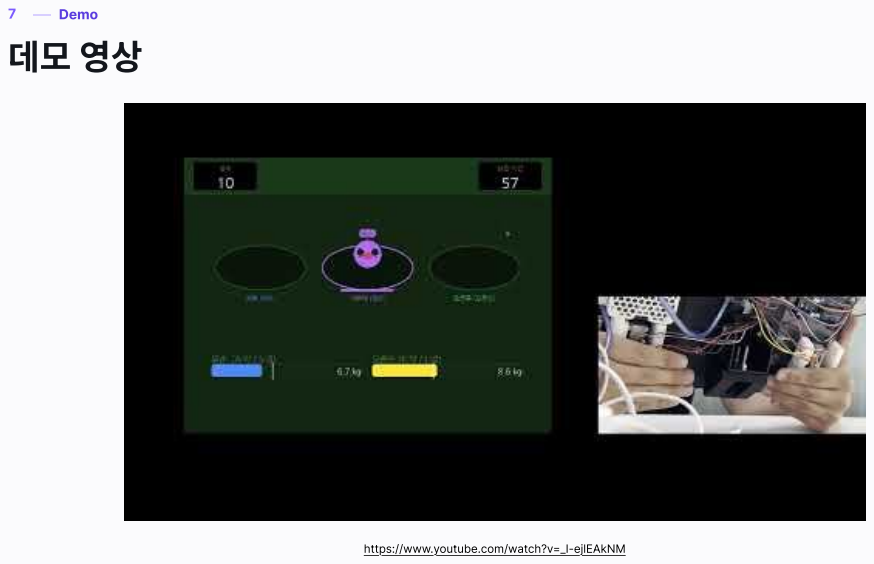
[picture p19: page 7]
Demo

https://www.youtube.com/watch?v=_I-ejlEAkNM

# 한계점 및 향후 개선

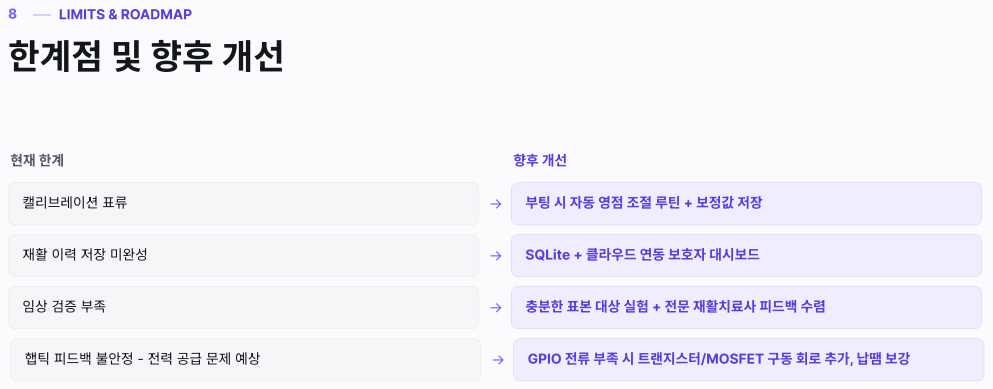
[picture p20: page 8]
LIMITS & ROADMAP; 캘리브레이션 표류; 부팅 시 자동 영점 조절 루틴 + 보정값 저장; SQLite + 클라우드 연동 보호자 대시보드; 충분한 표본 대상 실험 + 전문 재활치료사 피드백 수렴; 햅틱 피드백 불안정 - 전력 공급 문제 예상; GPIO 전류 부족 시 트랜지스터/MOSFET 구동 회로 추가, 납땜 보강

재활 이력 저장 미완성

# 감사합니다

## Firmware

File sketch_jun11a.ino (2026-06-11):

#define LEFT_DOUT   2
#define LEFT_SCK    3
#define RIGHT_DOUT  4
#define RIGHT_SCK   5

#define LEFT_VIB    9
#define RIGHT_VIB   10

#define BAUD_RATE        115200
#define SEND_INTERVAL_MS 10

long hx711_read(int dout, int sck) {
    while (digitalRead(dout) == HIGH);

    long value = 0;

    for (int i = 0; i < 24; i++) {
        digitalWrite(sck, HIGH);
        delayMicroseconds(1);
        value = (value << 1) | digitalRead(dout);
        digitalWrite(sck, LOW);
        delayMicroseconds(1);
    }

    digitalWrite(sck, HIGH);
    delayMicroseconds(1);
    digitalWrite(sck, LOW);
    delayMicroseconds(1);

    if (value & 0x800000) {
        value |= 0xFF000000;
    }

    return value;
}

bool hx711_ready(int dout) {
    return digitalRead(dout) == LOW;
}

long left_raw  = 0;
long right_raw = 0;
unsigned long last_send_ms = 0;

/* 비블로킹 시리얼 수신용 버퍼 */
static char serial_buf[8];
static int  serial_pos = 0;

void handle_serial() {
    while (Serial.available() > 0) {
        char c = (char)Serial.read();
        if (c == '\n' || c == '\r') {
            if (serial_pos == 2) {
                char side = serial_buf[0];
                char val  = serial_buf[1];
                if      (side == 'L' && val == '1') digitalWrite(LEFT_VIB,  HIGH);
                else if (side == 'L' && val == '0') digitalWrite(LEFT_VIB,  LOW);
                else if (side == 'R' && val == '1') digitalWrite(RIGHT_VIB, HIGH);
                else if (side == 'R' && val == '0') digitalWrite(RIGHT_VIB, LOW);
            }
            serial_pos = 0;
        } else if (serial_pos < 7) {
            serial_buf[serial_pos++] = c;
        } else {
            serial_pos = 0;
        }
    }
}

void setup() {
    Serial.begin(BAUD_RATE);

    pinMode(LEFT_DOUT,  INPUT);
    pinMode(LEFT_SCK,   OUTPUT);
    pinMode(RIGHT_DOUT, INPUT);
    pinMode(RIGHT_SCK,  OUTPUT);

    digitalWrite(LEFT_SCK,  LOW);
    digitalWrite(RIGHT_SCK, LOW);

    /* 진동 액츄에이터 핀 설정 */
    pinMode(LEFT_VIB,  OUTPUT);
    pinMode(RIGHT_VIB, OUTPUT);

    digitalWrite(LEFT_VIB,  LOW);
    digitalWrite(RIGHT_VIB, LOW);

    delay(400);
}

void loop() {
    /* 악력 센서 읽기 */
    if (hx711_ready(LEFT_DOUT)) {
        left_raw = hx711_read(LEFT_DOUT, LEFT_SCK);
    }
    if (hx711_ready(RIGHT_DOUT)) {
        right_raw = hx711_read(RIGHT_DOUT, RIGHT_SCK);
    }

    /* 시리얼 수신 — 라즈베리파이에서 진동 명령 받기
     * 포맷: "L1\n"  → 왼쪽 ON
     *       "L0\n"  → 왼쪽 OFF
     *       "R1\n"  → 오른쪽 ON
     *       "R0\n"  → 오른쪽 OFF
     */
    handle_serial();

    /* 10ms마다 악력 데이터 전송 */
    unsigned long now = millis();
    if (now - last_send_ms >= SEND_INTERVAL_MS) {
        last_send_ms = now;
        Serial.print(left_raw);
        Serial.print(',');
        Serial.println(right_raw);
    }
}

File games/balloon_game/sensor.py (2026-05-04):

"""
sensor.py
GripSensor 추상 인터페이스 + MockGripSensor / RealGripSensor / ArduinoGripSensor 구현

MockGripSensor    : PC 개발용 — 키보드(A/S 왼손, K/L 오른손)로 악력 시뮬레이션
RealGripSensor    : Raspberry Pi 실제 하드웨어용 (HX711 + 로드셀 GPIO)
ArduinoGripSensor : Arduino USB 시리얼용 — "raw1,raw2" 포맷 수신
"""

from __future__ import annotations
import threading
import time
from abc import ABC, abstractmethod
from collections import deque
from dataclasses import dataclass, field


# ── 설정 상수 ────────────────────────────────────────────────────────────────

SAMPLE_RATE_HZ   = 80      # HX711 80Hz 모드
DEADZONE_KG      = 1.0     # 1 kg 이하는 0으로 처리
SPIKE_THRESHOLD  = 8.0     # 이전 값 대비 8 kg 이상 급변 → 스파이크
MEDIAN_N         = 3       # 중간값 필터 윈도우
MOVING_AVG_N     = 5       # 이동평균 필터 윈도우
MOCK_STEP_KG     = 1.0     # Mock에서 키 1회 = 1 kg 변화량
MOCK_DECAY_HZ    = 8       # Mock에서 손 떼면 초당 감소량 (kg/s)


# ── 데이터 클래스 ─────────────────────────────────────────────────────────────

@dataclass
class GripReading:
    left_kg:  float = 0.0
    right_kg: float = 0.0
    timestamp: float = field(default_factory=time.time)


# ── 필터 파이프라인 ───────────────────────────────────────────────────────────

class GripFilter:
    """스파이크 → 중간값 → 이동평균 → 데드존 파이프라인"""

    def __init__(self):
        self._raw_buf:  deque[float] = deque(maxlen=MEDIAN_N)
        self._avg_buf:  deque[float] = deque(maxlen=MOVING_AVG_N)
        self._prev: float = 0.0

    def process(self, raw: float) -> float:
        # 1. 스파이크 필터
        if abs(raw - self._prev) > SPIKE_THRESHOLD:
            raw = self._prev
        self._prev = raw

        # 2. 중간값 필터
        self._raw_buf.append(raw)
        median = sorted(self._raw_buf)[len(self._raw_buf) // 2]

        # 3. 이동평균 필터
        self._avg_buf.append(median)
        avg = sum(self._avg_buf) / len(self._avg_buf)

        # 4. 데드존
        return 0.0 if avg < DEADZONE_KG else round(avg, 2)

    def reset(self):
        self._raw_buf.clear()
        self._avg_buf.clear()
        self._prev = 0.0


# ── 추상 인터페이스 ───────────────────────────────────────────────────────────

class GripSensor(ABC):

    def __init__(self):
        self._lock    = threading.Lock()
        self._reading = GripReading()
        self._running = False
        self._thread: threading.Thread | None = None

    def start(self):
        self._running = True
        self._thread = threading.Thread(target=self._loop, daemon=True)
        self._thread.start()

    def stop(self):
        self._running = False
        if self._thread:
            self._thread.join(timeout=1.0)

    def get(self) -> GripReading:
        with self._lock:
            r = self._reading
        return GripReading(r.left_kg, r.right_kg, r.timestamp)

    def _set(self, left: float, right: float):
        with self._lock:
            self._reading = GripReading(left, right)

    @abstractmethod
    def _loop(self): ...


# ── Mock 구현 (PC 개발용) ─────────────────────────────────────────────────────

class MockGripSensor(GripSensor):
    """
    키보드 입력으로 악력 시뮬레이션.
    Pygame 이벤트 루프에서 handle_keydown / handle_keyup 을 호출하세요.

    왼손:  A 누르면 증가 / S 누르면 감소  (또는 A 누르고 있으면 유지)
    오른손: K 누르면 증가 / L 누르면 감소
    """

    def __init__(self):
        super().__init__()
        self._left_target:  float = 0.0
        self._right_target: float = 0.0
        self._left_held:    bool  = False
        self._right_held:   bool  = False
        self._filter_l = GripFilter()
        self._filter_r = GripFilter()

    # Pygame 이벤트에서 호출
    def handle_keydown(self, key: int):
        import pygame
        if key == pygame.K_a:
            self._left_target  = min(30.0, self._left_target  + MOCK_STEP_KG)
            self._left_held    = True
        elif key == pygame.K_s:
            self._left_target  = max(0.0,  self._left_target  - MOCK_STEP_KG)
        elif key == pygame.K_k:
            self._right_target = min(30.0, self._right_target + MOCK_STEP_KG)
            self._right_held   = True
        elif key == pygame.K_l:
            self._right_target = max(0.0,  self._right_target - MOCK_STEP_KG)

    def handle_keyup(self, key: int):
        import pygame
        if key == pygame.K_a:
            self._left_held  = False
        elif key == pygame.K_k:
            self._right_held = False

    def set_grip(self, left_kg: float, right_kg: float):
        """슬라이더 등 외부 입력으로 직접 지정할 때 사용"""
        self._left_target  = max(0.0, min(30.0, left_kg))
        self._right_target = max(0.0, min(30.0, right_kg))

    def _loop(self):
        interval = 1.0 / SAMPLE_RATE_HZ
        decay    = MOCK_DECAY_HZ / SAMPLE_RATE_HZ  # 한 틱당 감소량

        while self._running:
            # 손 떼면 자연 감소
            if not self._left_held:
                self._left_target  = max(0.0, self._left_target  - decay)
            if not self._right_held:
                self._right_target = max(0.0, self._right_target - decay)

            lf = self._filter_l.process(self._left_target)
            rf = self._filter_r.process(self._right_target)
            self._set(lf, rf)
            time.sleep(interval)


# ── Real 구현 (Raspberry Pi + HX711) ─────────────────────────────────────────

class RealGripSensor(GripSensor):
    """
    실제 하드웨어 구현.
    calibration.json 에서 scale_factor / tare_offset 을 읽어옵니다.

    calibration.json 예시:
    {
        "left":  {"scale_factor": 420.5, "tare_offset": -12300},
        "right": {"scale_factor": 415.2, "tare_offset": -11900}
    }
    """

    # GPIO 핀 번호 (BCM 기준)
    LEFT_DOUT  = 5;  LEFT_SCK  = 6
    RIGHT_DOUT = 13; RIGHT_SCK = 19

    def __init__(self, calib_path: str = "calibration.json"):
        super().__init__()
        self._calib_path = calib_path
        self._filter_l   = GripFilter()
        self._filter_r   = GripFilter()
        self._scale_l    = 1.0
        self._tare_l     = 0
        self._scale_r    = 1.0
        self._tare_r     = 0
        self._load_calibration()

    def _load_calibration(self):
        import json, os
        if not os.path.exists(self._calib_path):
            print(f"[WARN] {self._calib_path} 없음 — 캘리브레이션 필요")
            return
        with open(self._calib_path) as f:
            data = json.load(f)
        self._scale_l = data["left"]["scale_factor"]
        self._tare_l  = data["left"]["tare_offset"]
        self._scale_r = data["right"]["scale_factor"]
        self._tare_r  = data["right"]["tare_offset"]
        print("[INFO] 캘리브레이션 로드 완료")

    def _loop(self):
        try:
            from hx711 import HX711  # pip install hx711
        except ImportError:
            print("[ERROR] hx711 라이브러리 없음. pip install hx711")
            return

        hx_l = HX711(dout_pin=self.LEFT_DOUT,  pd_sck_pin=self.LEFT_SCK)
        hx_r = HX711(dout_pin=self.RIGHT_DOUT, pd_sck_pin=self.RIGHT_SCK)

        # 80Hz 모드 설정 (RATE 핀 HIGH)
        for hx in (hx_l, hx_r):
            hx.set_reading_format("MSB", "MSB")
            hx.set_reference_unit(1)
            hx.reset()
            hx.tare()

        interval = 1.0 / SAMPLE_RATE_HZ

        while self._running:
            try:
                raw_l = (hx_l.get_raw_data_mean(times=1) - self._tare_l) / self._scale_l
                raw_r = (hx_r.get_raw_data_mean(times=1) - self._tare_r) / self._scale_r
                lf = self._filter_l.process(max(0.0, raw_l))
                rf = self._filter_r.process(max(0.0, raw_r))
                self._set(lf, rf)
            except Exception as e:
                print(f"[WARN] 센서 읽기 오류: {e}")
            time.sleep(interval)


# ── Arduino 구현 (USB 시리얼) ──────────────────────────────────────────────────

def _find_arduino_port() -> str:
    """USB에서 아두이노 포트 자동 감지"""
    try:
        import serial.tools.list_ports
        for port in serial.tools.list_ports.comports():
            if any(k in port.description.lower() for k in
                   ['arduino', 'usbmodem', 'usbserial', 'ch340', 'cp210']):
                return port.device
    except ImportError:
        raise RuntimeError("pyserial 없음. pip install pyserial")
    raise RuntimeError("아두이노를 찾을 수 없습니다. USB 연결을 확인하세요.")


class ArduinoGripSensor(GripSensor):
    """
    Arduino USB 시리얼 센서.
    아두이노가 115200 baud로 "raw1,raw2\\n" 형식의 정수값을 전송해야 합니다.

    시작 시 동작:
        1. 3초 영점(tare) 측정 — 아무것도 올려놓지 마세요
        2. 5초 최대악력 측정 — 최대한 세게 쥐어주세요 (자동 스케일)
    """

    BAUD_RATE  = 115200
    TARE_SECS  = 3
    CALIB_SECS = 5

    def __init__(self):
        super().__init__()
        self._filter_l = GripFilter()
        self._filter_r = GripFilter()
        self._tare_l   = 0.0
        self._tare_r   = 0.0
        self._scale_l  = 1.0
        self._scale_r  = 1.0
        self._port     = _find_arduino_port()
        print(f"[INFO] 아두이노 감지: {self._port}")

    def _read_raw(self, ser) -> tuple[int, int] | None:
        """시리얼에서 한 줄 읽어 (raw1, raw2) 반환. 실패 시 None."""
        try:
            line = ser.readline().decode('utf-8', errors='ignore').strip()
            if ',' in line:
                parts = line.split(',')
                return int(parts[0]), int(parts[1])
        except (ValueError, IndexError):
            pass
        return None

    def _do_tare(self, ser):
        print(f"[INFO] 영점 조절 중 ({self.TARE_SECS}초)... 센서에서 손 떼주세요!")
        buf_l, buf_r = [], []
        deadline = time.time() + self.TARE_SECS
        while time.time() < deadline:
            if ser.in_waiting:
                pair = self._read_raw(ser)
                if pair:
                    buf_l.append(pair[0])
                    buf_r.append(pair[1])
        self._tare_l = sum(buf_l) / len(buf_l) if buf_l else 0.0
        self._tare_r = sum(buf_r) / len(buf_r) if buf_r else 0.0
        print(f"[INFO] 영점 완료: L={self._tare_l:.0f}  R={self._tare_r:.0f}")

    def _do_scale_calib(self, ser, pop_kg: float):
        print(f"[INFO] 최대악력 측정 ({self.CALIB_SECS}초)... 최대한 세게 쥐어주세요!")
        max_l, max_r = 0.0, 0.0
        deadline = time.time() + self.CALIB_SECS
        while time.time() < deadline:
            if ser.in_waiting:
                pair = self._read_raw(ser)
                if pair:
                    max_l = max(max_l, abs(pair[0] - self._tare_l))
                    max_r = max(max_r, abs(pair[1] - self._tare_r))
        # 최대값이 pop_kg에 대응하도록 스케일 설정
        self._scale_l = max(max_l, 1.0) / pop_kg
        self._scale_r = max(max_r, 1.0) / pop_kg
        print(f"[INFO] 스케일 설정: L={self._scale_l:.1f}  R={self._scale_r:.1f}")

    def _loop(self):
        try:
            import serial
        except ImportError:
            print("[ERROR] pyserial 없음. pip install pyserial")
            return

        try:
            ser = serial.Serial(self._port, self.BAUD_RATE, timeout=1)
            time.sleep(2)           # 아두이노 부팅 대기
            self._do_tare(ser)
            self._do_scale_calib(ser, pop_kg=22.0)
            print("[INFO] 게임 시작!")

            interval = 1.0 / SAMPLE_RATE_HZ
            while self._running:
                if ser.in_waiting:
                    pair = self._read_raw(ser)
                    if pair:
                        raw_l = (pair[0] - self._tare_l) / self._scale_l
                        raw_r = (pair[1] - self._tare_r) / self._scale_r
                        lf = self._filter_l.process(max(0.0, raw_l))
                        rf = self._filter_r.process(max(0.0, raw_r))
                        self._set(lf, rf)
                else:
                    time.sleep(interval)
        except Exception as e:
            print(f"[ERROR] 아두이노 오류: {e}")
        finally:
            try:
                ser.close()
            except Exception:
                pass

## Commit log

2026-05-04 게임 및 파일정리
    [Base_1.stl, HX711_Load_Cell--Foot.stl, console.3mf, console.stl]
2026-05-22 라즈베리파이도 되게
2026-06-11 진동연동
2026-06-11 r게임 나갈수도 있게
2026-06-15 최종최종
2026-06-15 설명 추가
